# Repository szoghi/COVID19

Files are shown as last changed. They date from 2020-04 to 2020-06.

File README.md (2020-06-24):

# COVID19
Open-source files to 3D print Fresno State face shields, PAPR machines using retrofitted CPAP machines, masks with emergency FDA approval by Barrow Neurological, and emergency vent splitters and flow limiters.

We advise using 8.5"x14" transparency films and velcro to stick to the shield, along with an elastic strap to provide a comfortable way of securely mounting the shield assembly. Plastic shields can be sanitized and reused. They are designed to allow healthcare providers room to also wear googles and N95 masks.

http://www.fresnostatenews.com/2020/04/16/engineering-students-alumni-develop-protective-equipment-for-health-care-professionals/

Face shield stacks printed at the Fresno State engineering labs
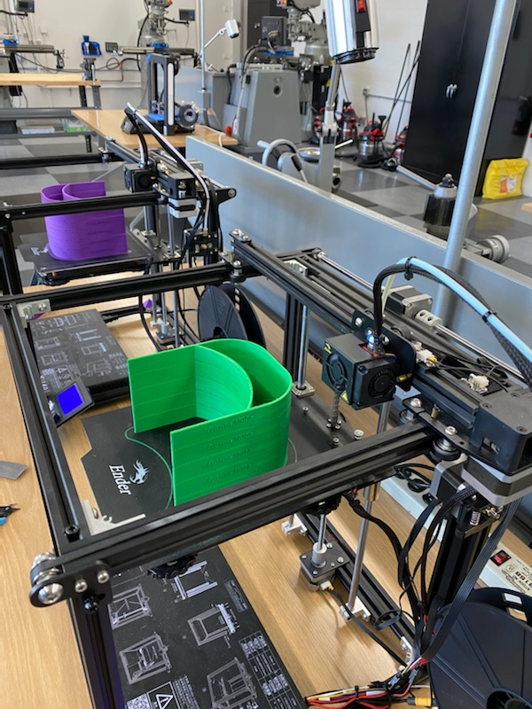
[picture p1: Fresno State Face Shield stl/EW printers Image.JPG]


PAPR machine retrofitted from an old CPAP machine. It can provide continuous filtered air (P100-rated filters) to medical providers
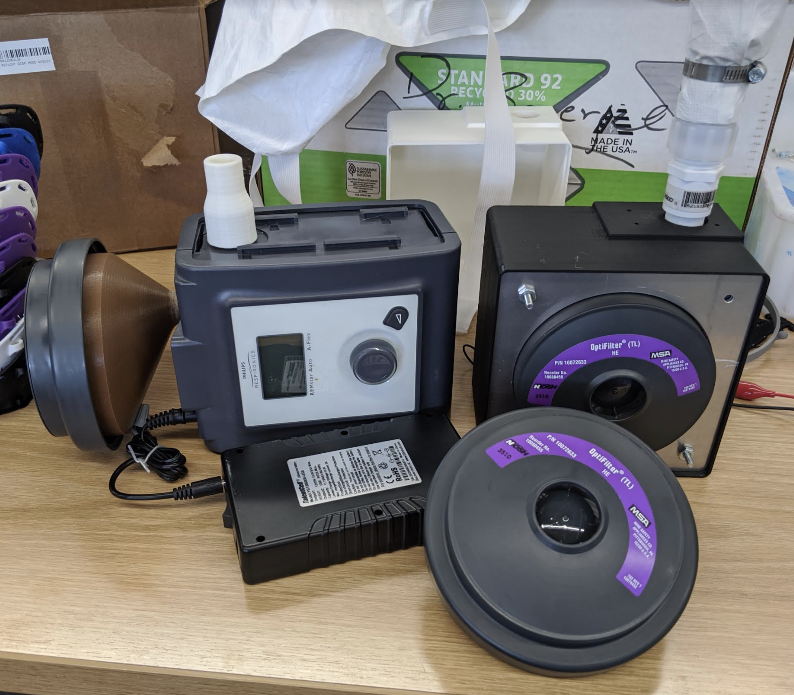
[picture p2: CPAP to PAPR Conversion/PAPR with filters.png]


UCSF Fresno's Dr. Eric Day testing the PAPR machine
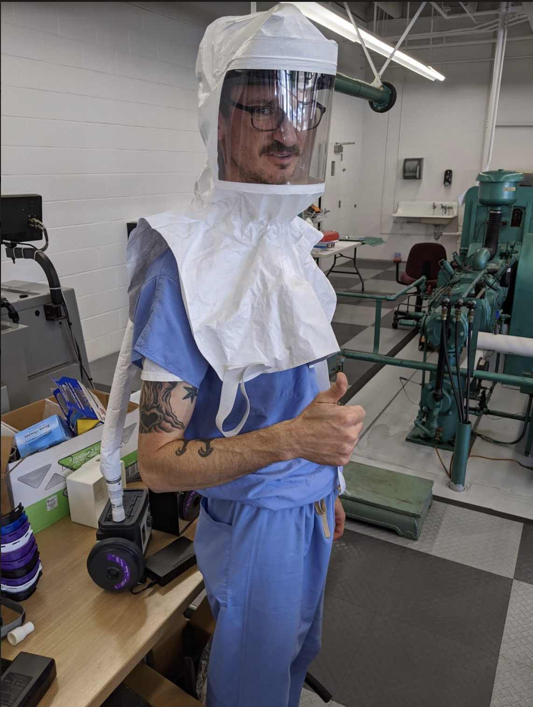
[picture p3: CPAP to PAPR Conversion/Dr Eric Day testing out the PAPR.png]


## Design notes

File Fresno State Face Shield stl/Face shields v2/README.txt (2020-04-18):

This version has a thickness of .09 inch verse .1 inch. For the printers we are using (mostly Ender3 and Ender5) we found that this took 
away a small crack in the middle of the band and actually made it stronger. 

If you are able to edit the Solidworks 2019 part file, you can create stacks of whatever size you desire by editing the linear pattern component.
Also, it is possible to suppress or delete the first extrude cute to remove the "FRESNO STATE" logo to save print time.

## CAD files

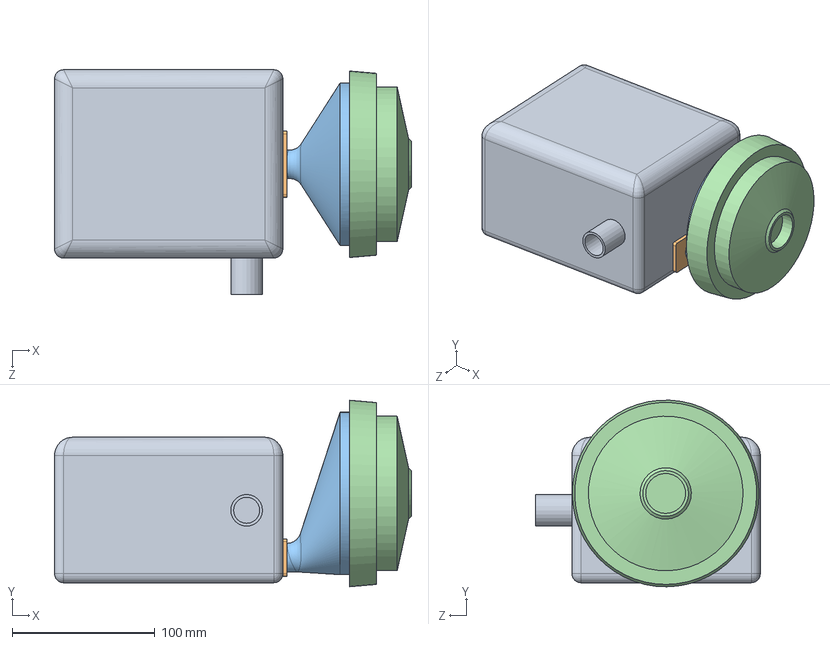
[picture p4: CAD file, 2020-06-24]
CPAP to PAPR Conversion/Assembly - CPAP machine with Optifilter.SLDASM
250.1 x 130.7 x 157.4 mm
CPAP machine
Cap for Phillps blower
Filter holder for phillips-1
filter

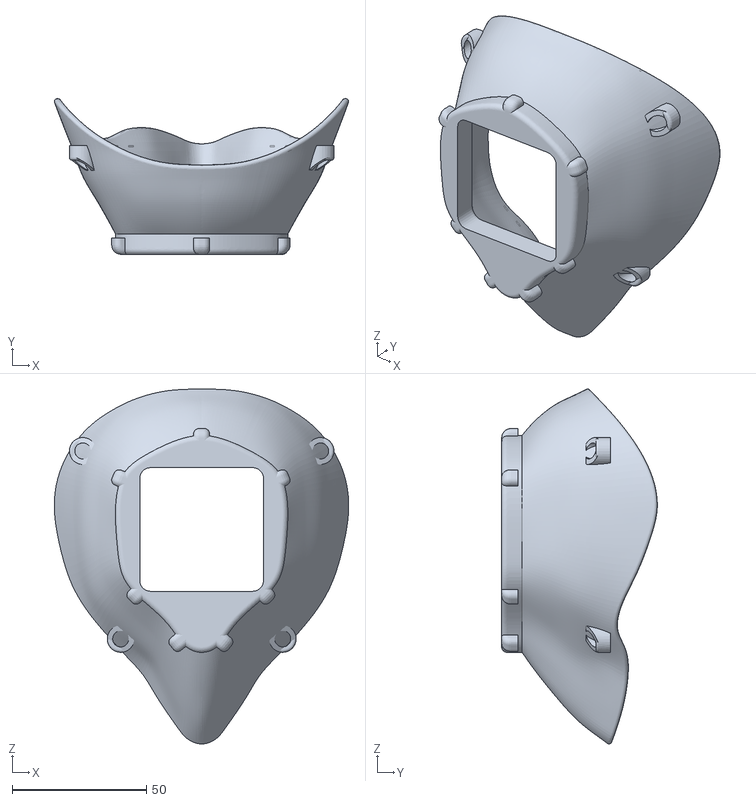
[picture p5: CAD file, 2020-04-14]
Barrow FDA EM approved mask/MontanaMask shielded.stl
109.5 x 57.9 x 132.0

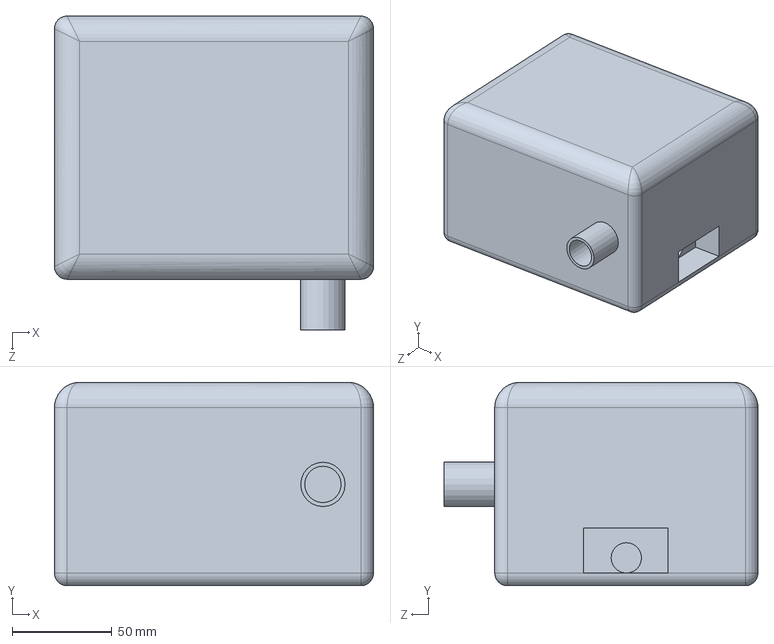
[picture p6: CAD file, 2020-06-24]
CPAP to PAPR Conversion/CPAP machine.SLDPRT
160.0 x 102.0 x 157.4 mm

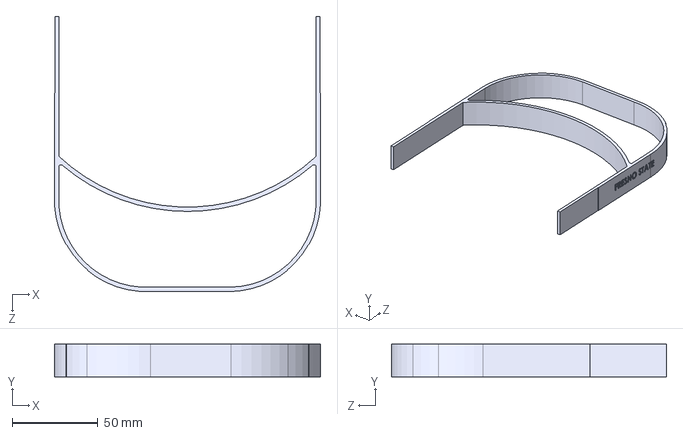
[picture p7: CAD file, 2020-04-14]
Fresno State Face Shield stl/Face shield stacks/1.STEP
155.0 x 19.1 x 160.1 mm

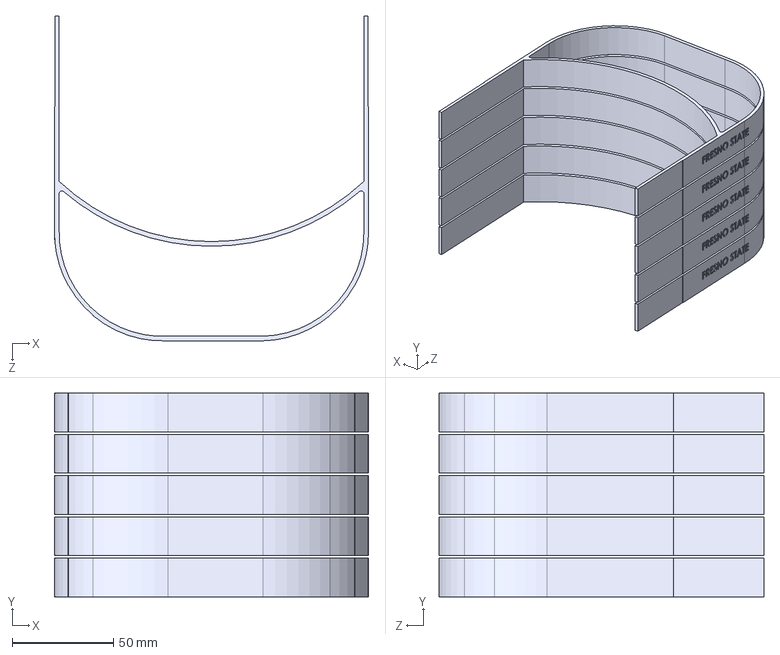
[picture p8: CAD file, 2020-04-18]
Fresno State Face Shield stl/Face shields v2/1.STEP
154.7 x 100.3 x 160.0 mm

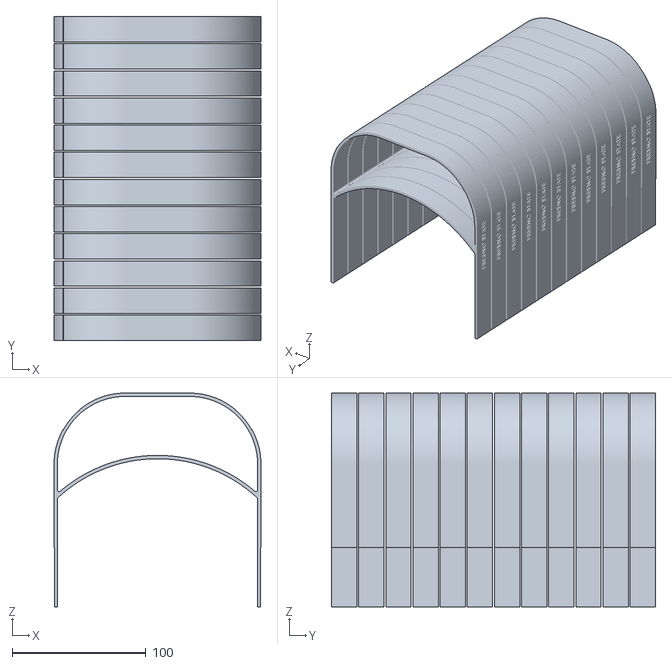
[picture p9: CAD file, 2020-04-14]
Fresno State Face Shield stl/Face shield stacks/Stack of 12.STL
155.0 x 242.6 x 160.1

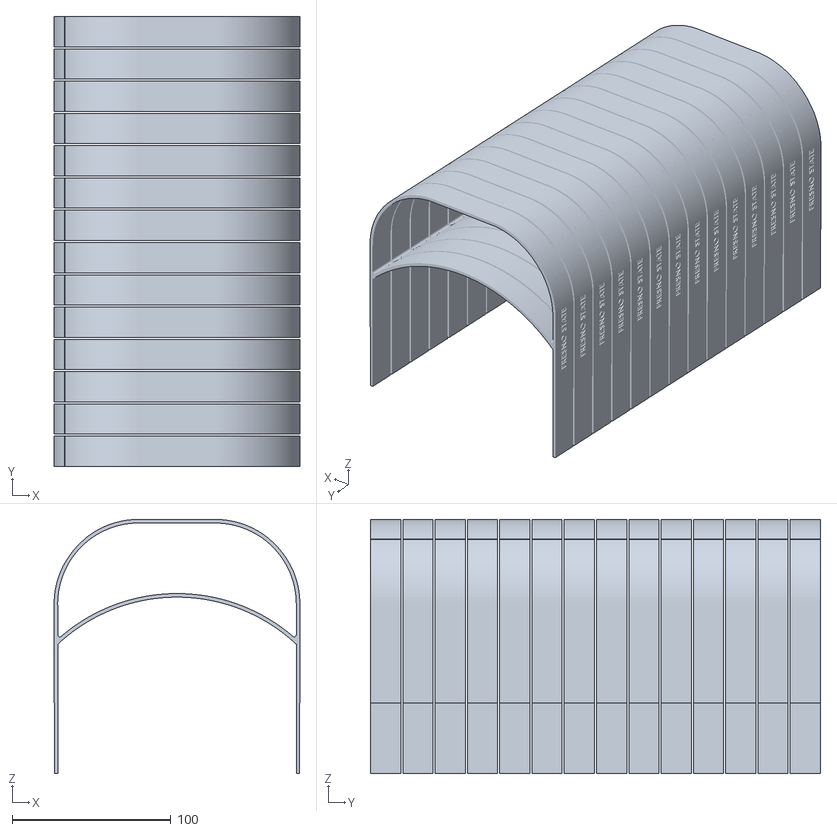
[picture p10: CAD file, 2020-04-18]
Fresno State Face Shield stl/Face shields v2/14.STL
154.7 x 283.2 x 160.0

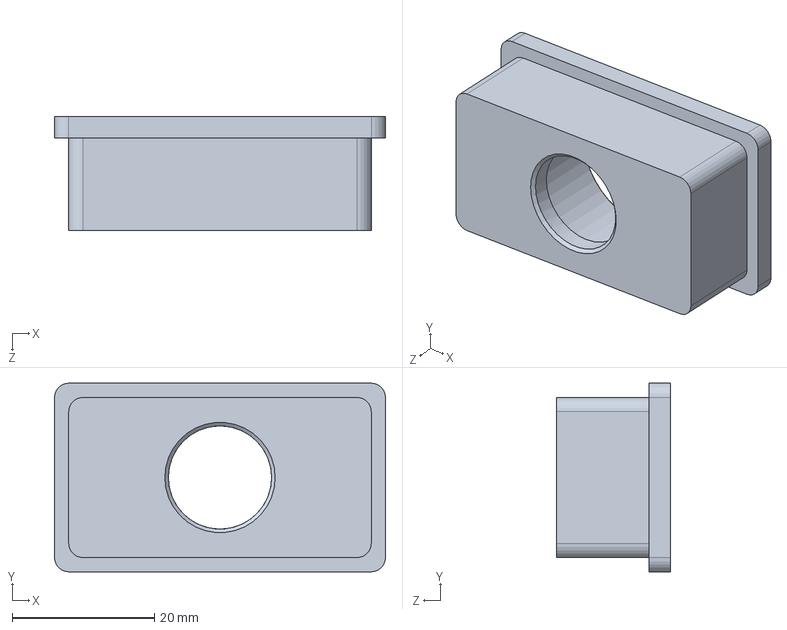
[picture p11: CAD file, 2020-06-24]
CPAP to PAPR Conversion/Cap for Phillps blower.SLDPRT
46.5 x 26.5 x 16.0 mm

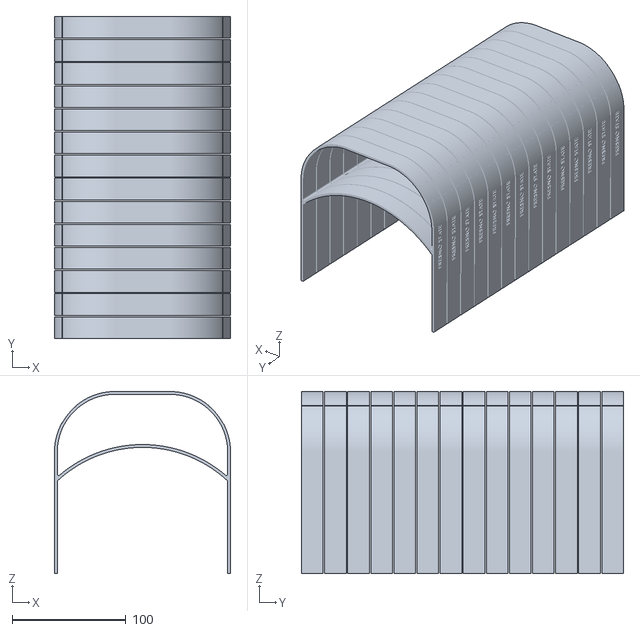
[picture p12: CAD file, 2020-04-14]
Fresno State Face Shield stl/Face shield stacks/Stack of 14.STL
155.0 x 283.2 x 160.1

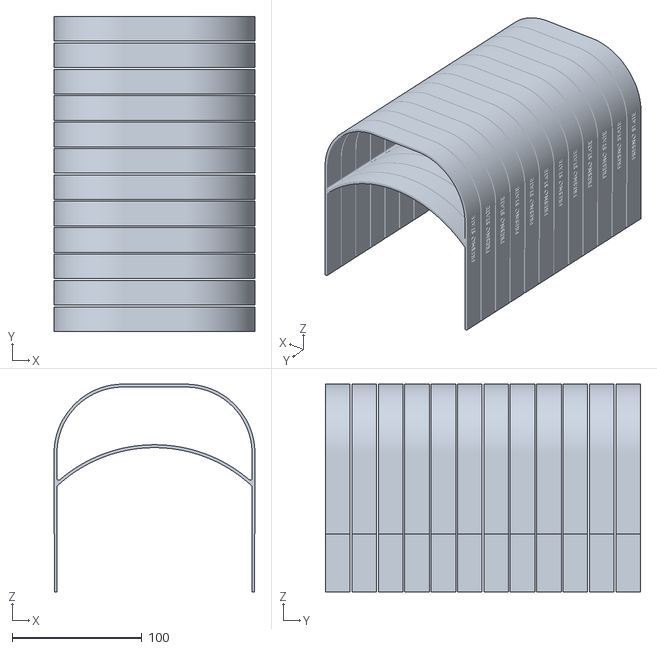
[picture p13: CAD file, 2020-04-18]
Fresno State Face Shield stl/Face shields v2/12.STL
154.7 x 242.6 x 160.0

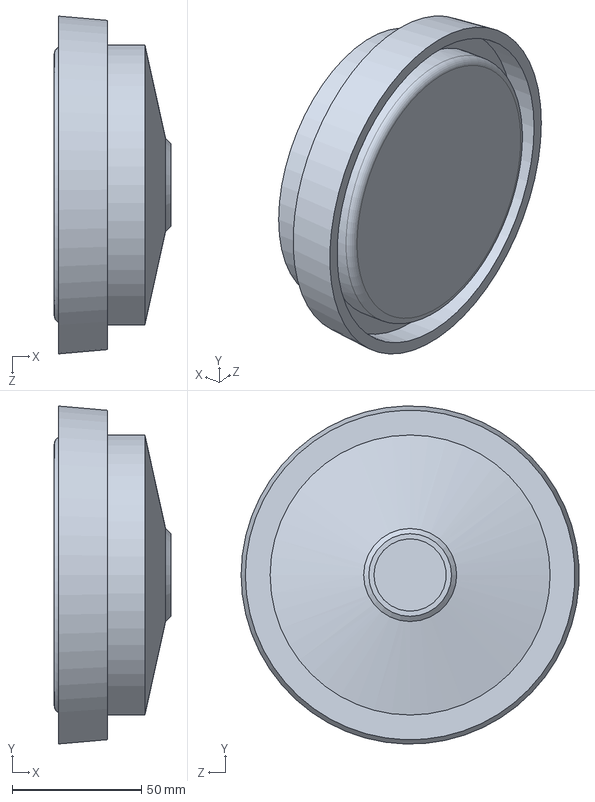
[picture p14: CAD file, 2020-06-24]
CPAP to PAPR Conversion/filter.SLDPRT
45.1 x 130.7 x 130.7 mm

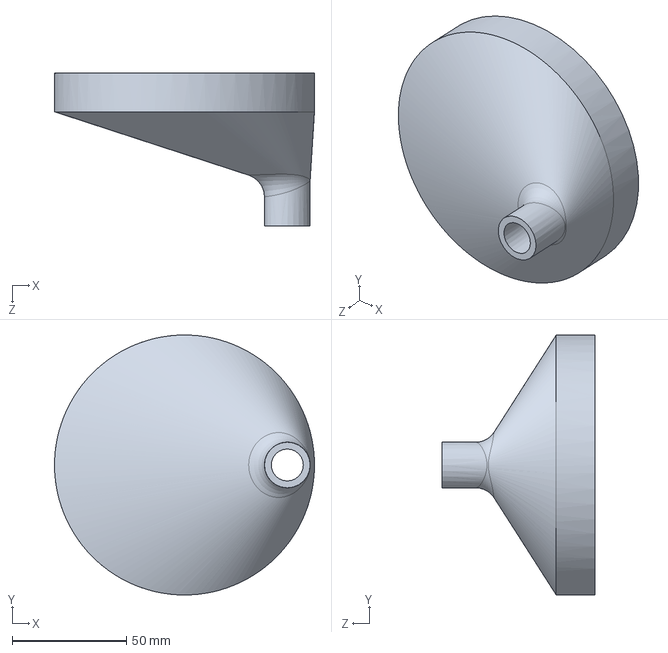
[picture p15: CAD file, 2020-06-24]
CPAP to PAPR Conversion/Filter holder for phillips-1.SLDPRT
113.8 x 113.8 x 67.0 mm

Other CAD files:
Fresno State Face Shield stl/Fresno State Shield.STL
Fresno State Face Shield stl/Face shield stacks/Stack of 5.STEP
Fresno State Face Shield stl/Face shields v2/5.STEP
Fresno State Face Shield stl/Face shield stacks/1.SLDPRT
Fresno State Face Shield stl/Face shield stacks/1.STL
Fresno State Face Shield stl/Face shield stacks/Stack of 5.STL
Fresno State Face Shield stl/Face shields v2/1.SLDPRT
Fresno State Face Shield stl/Face shields v2/1.STL
Fresno State Face Shield stl/Face shields v2/5.STL

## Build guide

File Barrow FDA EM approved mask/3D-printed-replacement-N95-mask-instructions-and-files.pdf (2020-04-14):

# 3D Printed N95 Replacement Mask

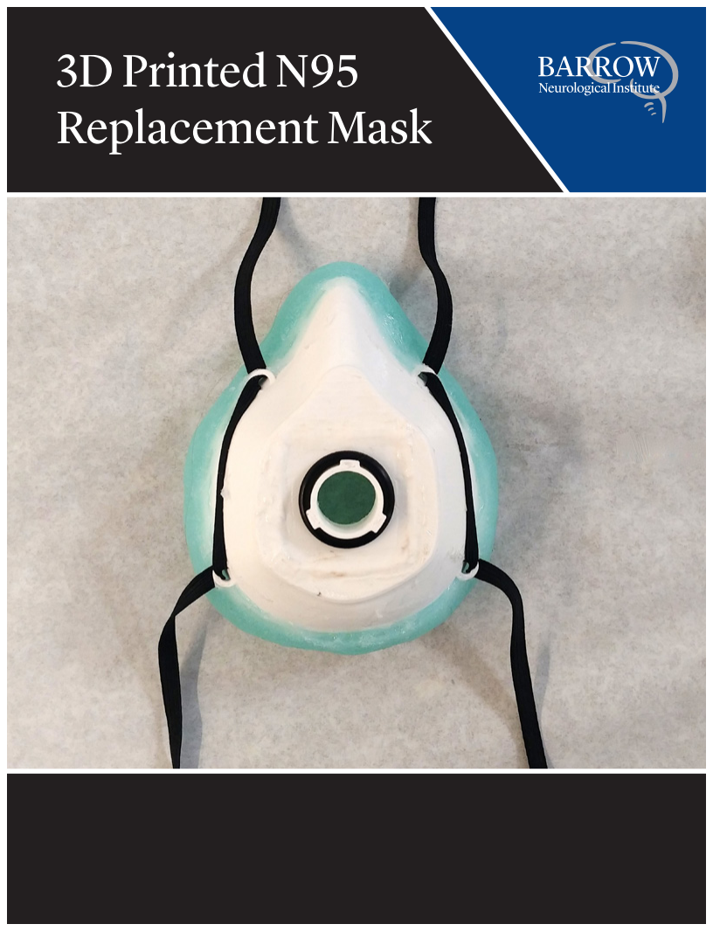
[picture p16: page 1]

## 3D Printed N95 Replacement Mask

## Table of Contents

## Legal Disclosure

The products and claims made herein have not been evaluated by the United States Food and Drug Administration and may not provide the same level of protection as FDA-cleared surgical masks, N95 masks, and equivalents.

## Acknowledgements

The designs in this booklet were created by the team at the Barrow Innovation Center, a rapid prototyping laboratory within Barrow Neurological Institute, in collaboration with SurgiSTUD LLC. The team made many adjustments to existing designs and files freely available online at makethemasks.com.

What follows are the published improvements to the mask design.

## Bill of Materials

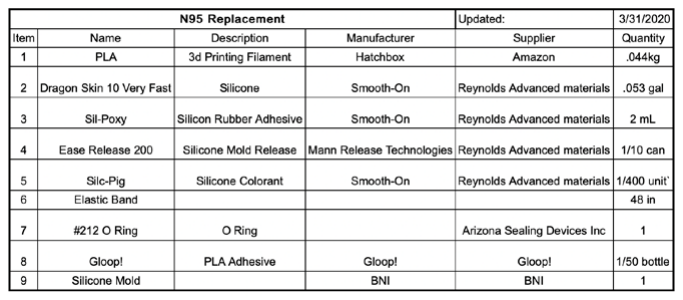
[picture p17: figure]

## Printing Parts

All 3D printing files can be found in our github repository here. (https://github.com/BarrowNeurological/COVID-19)

These files can be downloaded to work with any 3D printer. At the Barrow Innovation Center we’ve been using FDM printers as they’ve proven to be fast and reliable.

Recommended print settings:
-Material: PLA
-Infill: >20%
-Shells: >4 (1.6mmm)

Scale mask 90% if making a mask for a person with a smaller face and print the corresponding filter.

## Preparing Mask For Silicone Mold Creation

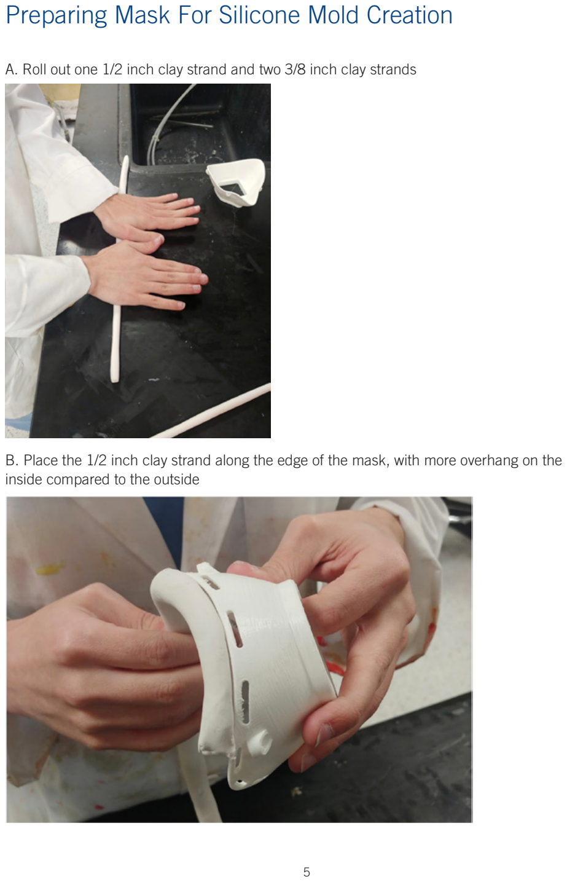
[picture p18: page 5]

A. Roll out one 1/2 inch clay strand and two 3/8 inch clay strands
B. Place the 1/2 inch clay strand along the edge of the mask, with more overhang on the inside compared to the outside

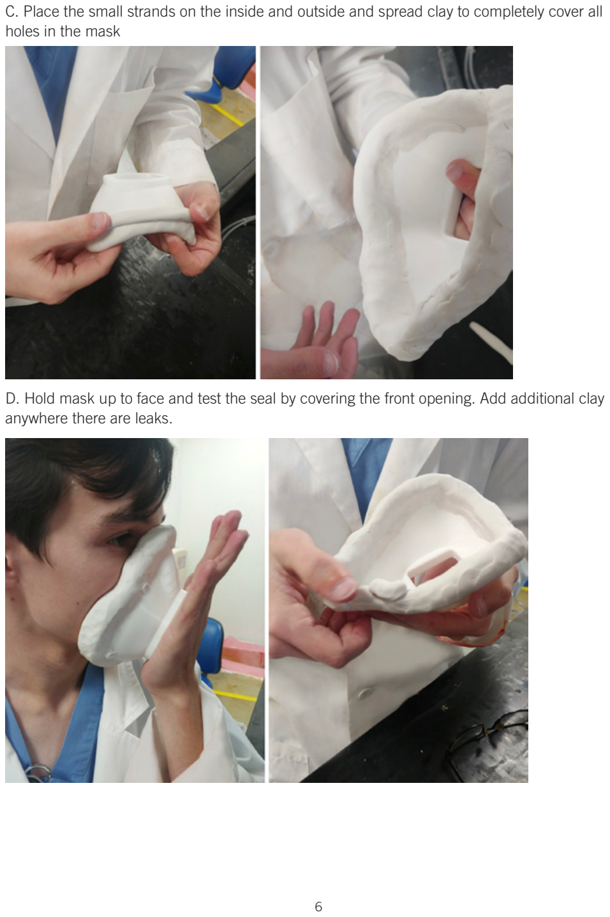
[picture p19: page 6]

C. Place the small strands on the inside and outside and spread clay to completely cover all holes in the mask
D. Hold mask up to face and test the seal by covering the front opening. Add additional clay anywhere there are leaks.

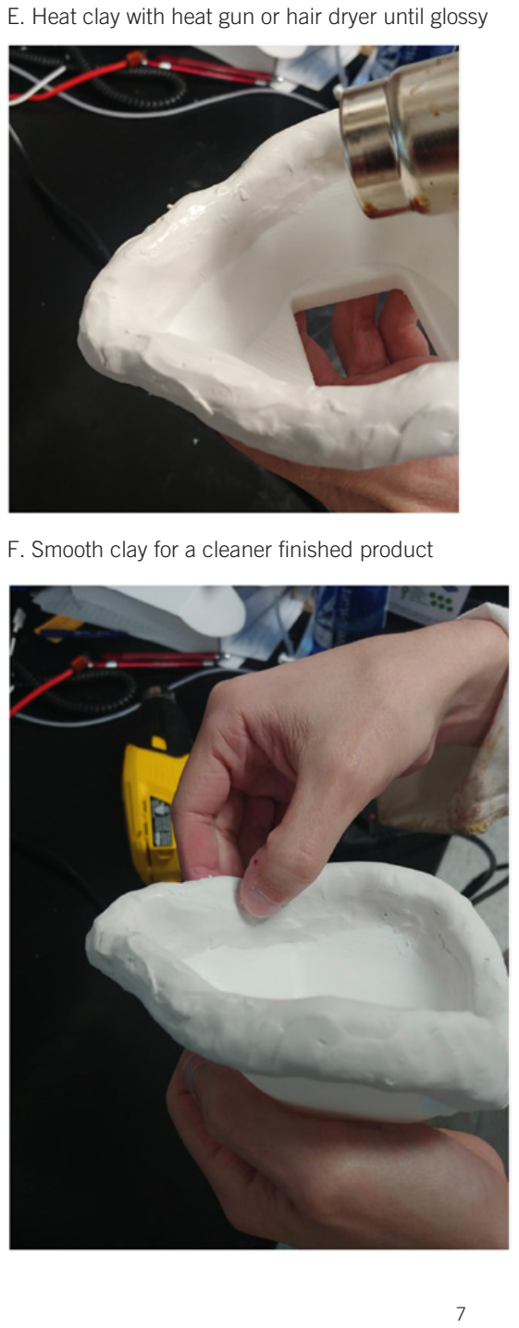
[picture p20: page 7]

E. Heat clay with heat gun or hair dryer until glossy
F. Smooth clay for a cleaner finished product

## Creating a Silicone Mold

A. Spray prepared mask with mold release

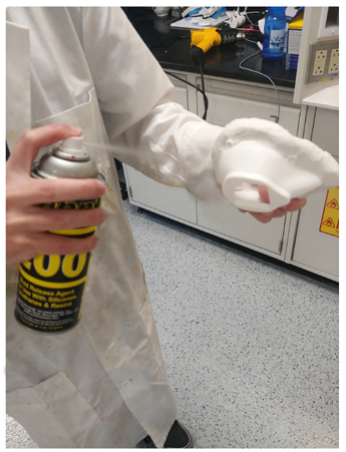
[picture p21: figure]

B. Find a tupper ware container that fits the mask
C. Mix enough silicone to fill container with at least ¼ inch of silicone
D. Pour silicone in container and allow to cure
E. Mix enough silicone to fill container enough to cover all clay parts of mask
F. Place mask in container and pour silicone around mask until all clay is covered

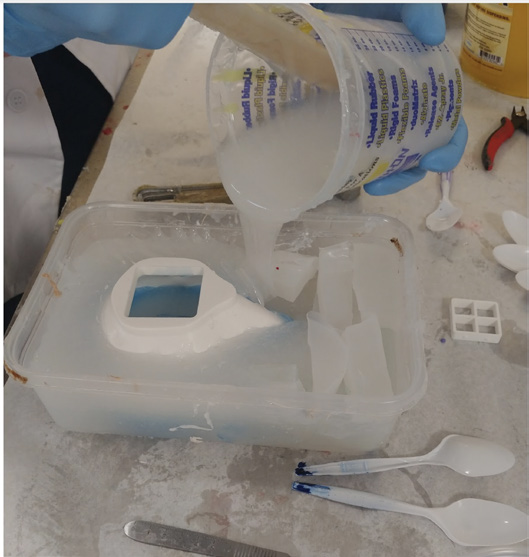
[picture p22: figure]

Optionally: add pegs on all four corners to make following steps easier and fill gaps with filler to save silicone

G. Allow silicone to cure
H. Mix enough silicone to fill the inside of the mask
I. Pour silicone through the square hole of the mask until the mask is filled, avoid silicone spilling over sides of mask

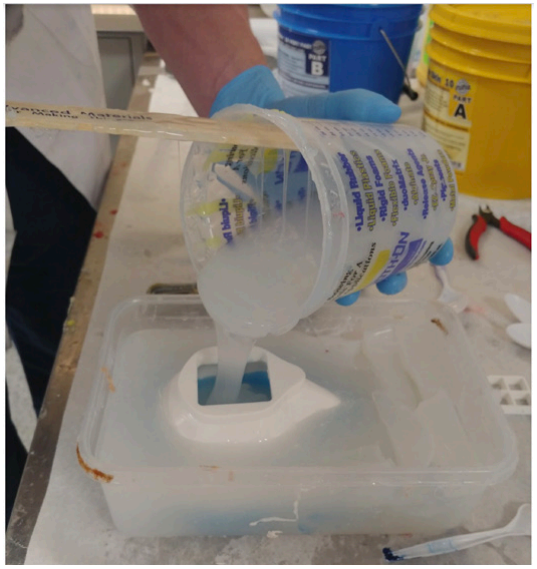
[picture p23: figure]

J. Allow silicone to cure
K. Carefully remove mask from silicone mold, ensuring that all clay has been removed

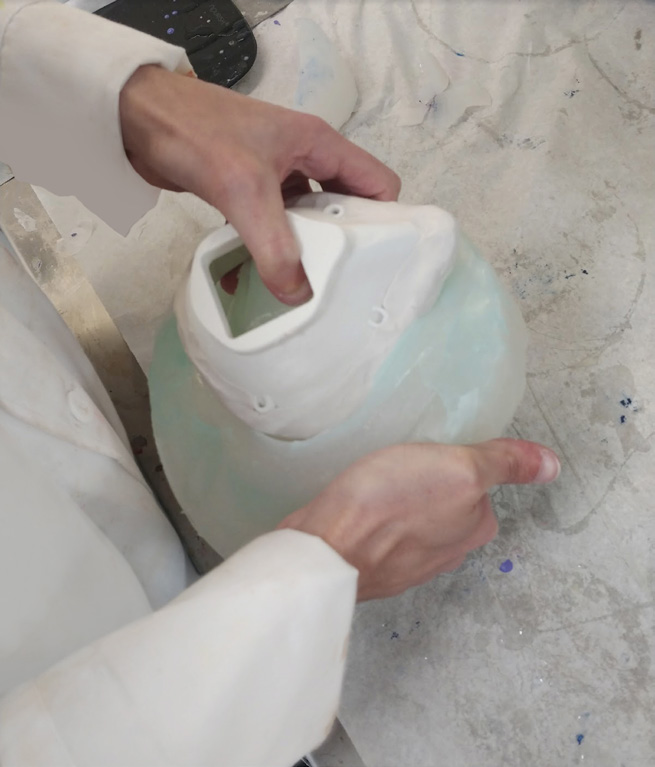
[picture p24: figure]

## Casting Silicone Seal

A. Use a newly printed mask or a mask cleaned of all clay, visually inspect for print imperfections that might impair mask performance
B. Spray the inside and top of the silicone mold with wax mold release, pulling back edges of mold to spray inside of mold to ensure a good coating on the interior
ii. Avoid touching interior surfaces coated with mold release as it can be wiped off
C. Mix enough silicone to fill mold:
-Approximately 200ml total for Montana Mask printed at 100% Scale -Approximately 150ml total for Montana Mask printed at 90% Scale
-Optionally add colorant to personalize masks or identify different sizes
D. Pull back edges of mold and pour in silicone until interior is full

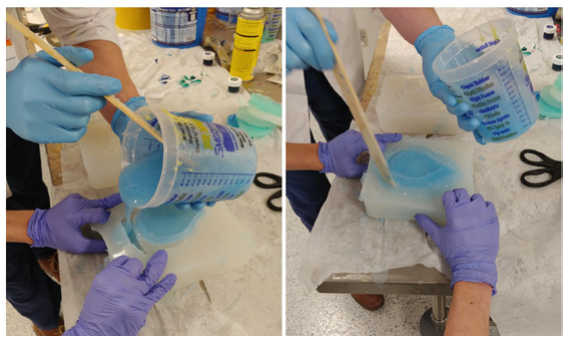
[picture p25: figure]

E. Place mask in mold

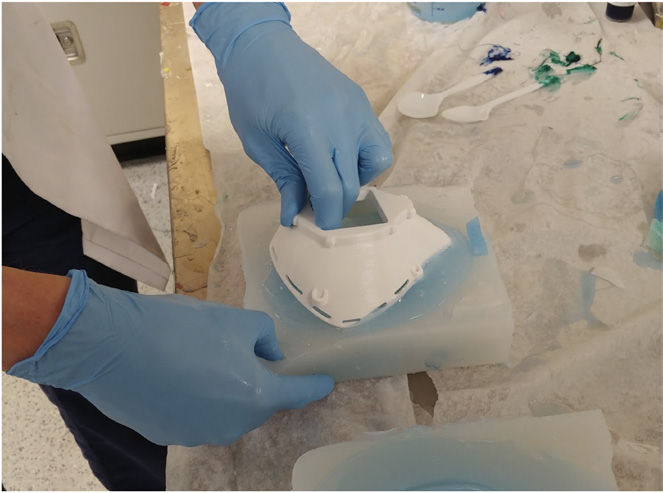
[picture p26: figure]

F. Allow silicone to cure
G. Carefully remove mask from mold:
i. Attempt to get one finger in and underneath the silicone seal of the mask
ii. Run finger around mask entire mask underneath the silicone seal, detethering any point where silicone seal adhered to silicone mold
iii. Once finger can be run freely around entire mask, get multiple fingers underneath nose of mask and carefully pull out mask, detethering any interior adhesions as necessary

## Mask Post Processing

H. Remove any excess material from mask with a sharp blade

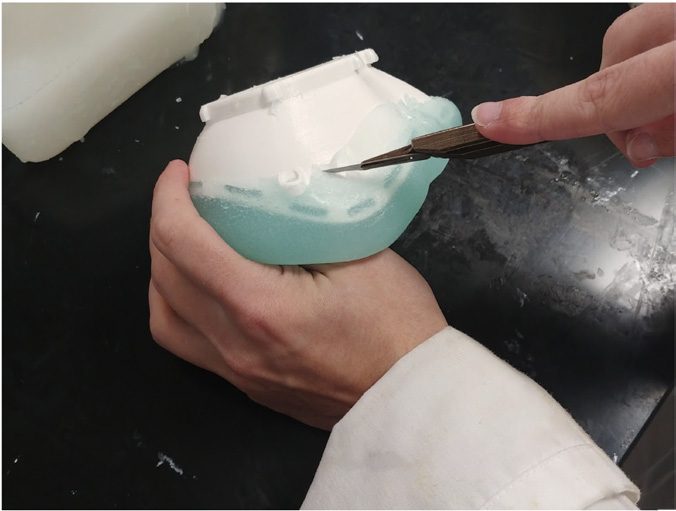
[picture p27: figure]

I. If silicone does not fill all slits around edge of mask:
J. Mix a small batch of silicone and apply to sites where desired, filling holes completely
ii. It may be necessary to allow silicone to become more viscous before applying
iii. A heat gun (or blow dryer) can also be used to accelerate the curing and prevent running of silicone
iv. Allow silicone to cure
K. Use silicone glue to seal down edges of silicone seal on the outside of the mask

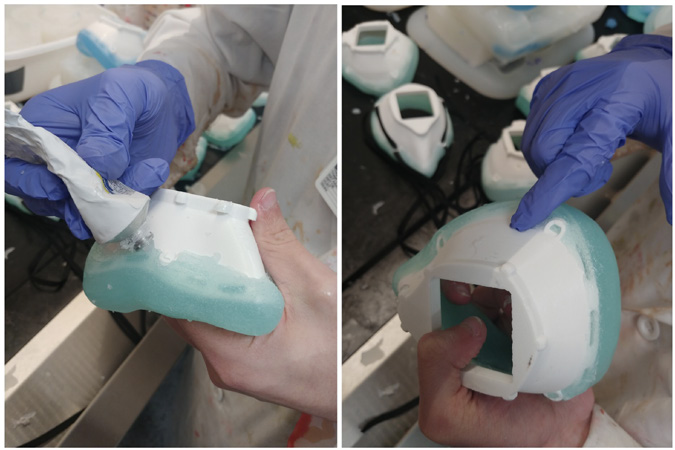
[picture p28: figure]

i. This will make the mask easier to clean ii. Allow silicone glue to cure

## Attaching Filter Coupler

A. Insert coupler into mask, ensuring that the filter will be oriented correctly when installed, press in until flush with mask

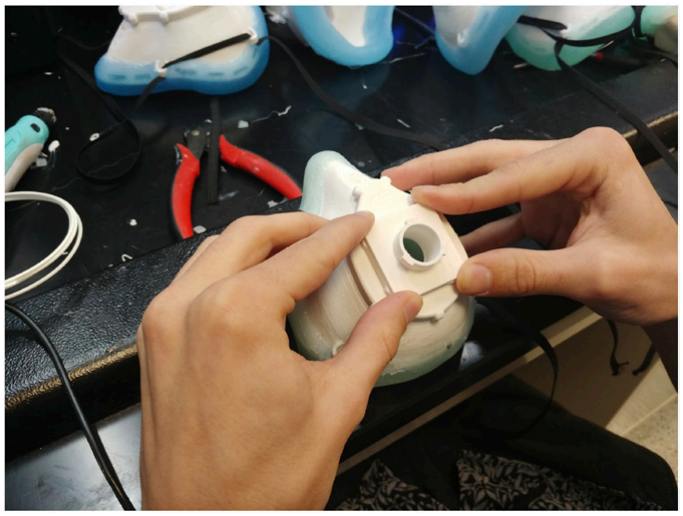
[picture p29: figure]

B. Use a 3-D printing pen to add a thin line of PLA across seam between mask and coupler

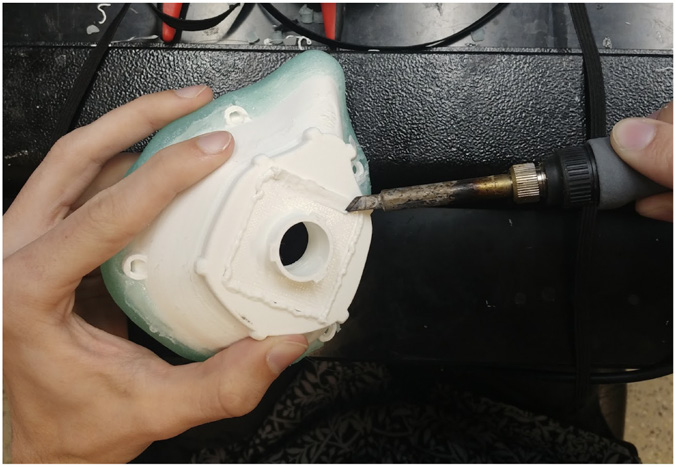
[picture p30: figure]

C. Install O-Ring over coupler

## Attaching Straps

A. Use sharp blade to cut through silicone covering strap connectors and remove any silicone inside of connectors
B. Measure and cut 48” of elastic material
C. Burn ends of elastic material to avoid fraying
D. Feed elastic through connectors in the following order:
i. Bottom left > upper left > upper right > bottom right

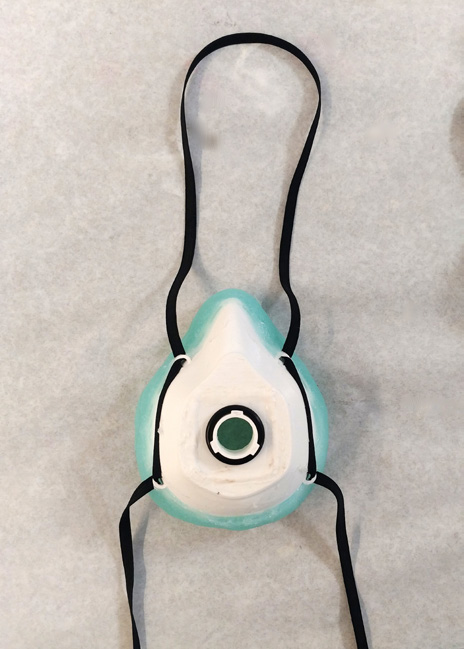
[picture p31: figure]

## Fitting and Testing

Testing of these masks can be done in two steps: suction and saccharin (standard fit test).

For suction, fit the finished mask to your face. Cover the coupler hole with your palm and inhale lightly. If there is a complete seal, you will not be able to inhale.

The mask can undergo the same routine fit test as the standard FDA approved N95 surgical mask. This involves the standard saccharin nebulizers and testing hoods. This test and its details can be found on the OSHA website.

Guidelines for Fit Testing
This test and its details can be found on the OSHA website here. (https://www.osha.gov/laws-regs/regulations/standardnumber/1910/1910.134AppA)

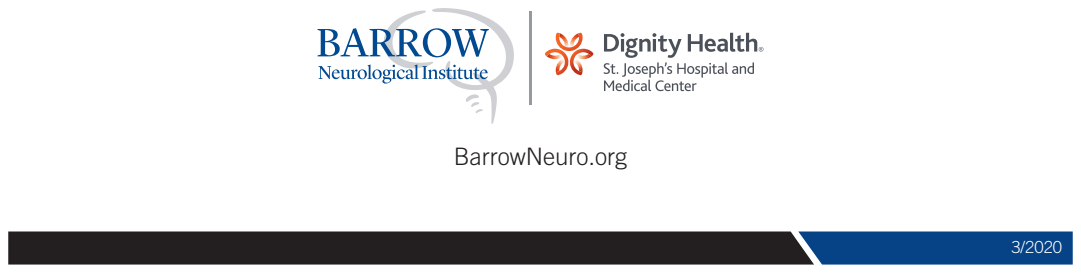
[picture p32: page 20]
BarrowNeuro.org
